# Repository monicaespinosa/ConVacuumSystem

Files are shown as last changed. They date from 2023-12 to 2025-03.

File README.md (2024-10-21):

# ConVacuumSystem
Later I will have time to explain what this is about. Let's start with the important things.

## Current circuit
The circuit (still to try) goes as following:



The setup still has to be simulated to find out V_c and to check the accuracy of the voltages selected for the grid and the plate.

## CST Simulations of the setup
The following setup was simulated:


Initially were the following voltages set:
* V_S 6.4 V
* V_C: 6.4 V
* V_G= 400 V
* V_P= 1000 V

The result for the obtained trajectory is shown below. The obtained current was around 5 mA.



However, the shape of the electron beams seems to change its shape in a very drastic way. Making the V_C smaller (more negative) should help concentring more the electrons to the center of the beam. A second simulation was made sweeping the voltage of the Wehnelt_Cylinider between -10 V and 6 V. 

As a result, the following charges on the plate were obtained:


Particles that come out of the coil:


They are only high when the voltage at the Wehnelt Cylinider is equal or higher than that of the coil. A new simulation sweeping Vc between 6.4V and 15.4V is been made. Results:



Evidently, the current (and as a consequence the particles getting to the plate) exists only when V_C>=V_S. The trajectories of the particles change however as they seem to be pushed into the cylinder (because of the higher voltage):



A new simulation setting the voltage on the grid V_G=800 V, putting a porcelain cylinder around the components (to simulate the glass cylinider) and moving the cylinider along the z-axis was made. The obtained trajectories are:



### Setting the voltage on the plate nearly to 0
Simulation with V_G = 1000 V and V_P = 4 V, and moving the cylinder to its initial position.



Simulation with the same parameters but moving the cylinder so its positioned closer to the plate.



Final simulation moving the cylinder back again and setting its voltage to -V_S.



### Variations of the voltage on the plate

Current incoming to the plate is the import_2 current.


Incoming particles:


### Changing the cathode
For all the following simulations the following voltages are set: V_S=6.4V, V_C=-30V V_G = 1000V and V_P = 4V.

#### Vertical filled PEC cylinder
Model:



Trajectories:



Total current leaving the cathode: 1.191e-03 mA

### Vertical hollow PEC cylinder
The cathode looks like the one before but is hollow with a thickness of 0.3 mm.

Trajectories:



Total current leaving the cathode: 9.14e-02 mA

### Toroid
Model:



Trajectories:



Total current leaving the cathode: 0.98 mA

### Rectangular cathode:
Model:



Trajectories: 



Total current leaving the cathode: 0.78 mA

### Sphere
Model:



Trajectories:



Total current leaving the cathode: 1.19 mA

### cut Cone:
Model:



It didn't emit any current when being put this way. However, when rotating like this:



The following trajectories are gotten:



Total current leaving the cathode: 0.71 mA

### Electron-gun Cathode
Model: 



It's a "cone" whose two planar circular faces are connected not by a rotated linear surface but a rotated exponential surface so it's internal radious get's thicker in an exponential way along the w axis as w decreases, simulating a pointy trunked cone. It was initially made small but only few particles were accelerated. Increasing its size and getting it closer to the grid produces the following trajectories:



The total current leaving the cathode was 9.35 mA. However the trajectories are messy and very disperse. After trying to move both the cathode and the grid further from the plate, because of the Wehnelt-Cylinder, the particles collide and then get dispersed again, without reaching the plate:



### Toroid-Coil

Model:

Trajectories: (actually a pretty straight beam)



However, the current incoming to the plate was not as high as expected. In this case, a variation of the voltage on the plate was made and the following curve obtained:



A dependency of the current to the voltage on the grid was also tested. The results below show in fact that the highest this voltage is, the highest the current.



As the shape of the beam seems to be well centered, another try using two toroids was given a shot. The model of the cathode goes as following:



As expected, the trajectories:



However the current across the platte is 50 uA. 

### Clapton Coil
This is the coil used normally for vapers. One of these was modelled in CST and looks like this:




The current incoming into the plate is 21.46uA. However, as the clapton coils that are found in the market have typically a diameter of 3.0mm, which for this project is too small. In order to increase the size of the cathode, a few of them can be placed together. For this purpose, four clapton coils forming a loop was simulated:



Trajectories: Not so straight directed to the center of the beam.



Current incoming to the plate: 0.18 mA

## Current measurement

### Methode
As mentioned before, this is the electrical structure of the setup:



The current measurement in between the plate and the voltage source V_p is more detailed here:



The current flowing through R_mess is theorically expected to be around 5mA according to the simulations. Supposing that the current is 10mA, the following circuit was simulated to choose the value of R_mess:





The voltage across Rm increases as Rm does. A value of Rm=140 ohm is temporarily chosen.

The following component is a amplifier that measures the voltage across the resistor R_mess and whose output is a digital signal whose amount of 1's is proportional to the current flowing through R_mess. The used amplifier is the Si8946A, that measures voltages between -62.5 mV and +62.5 mV, and whose output has a frequency of 10MHz. As this frequency is too high for a microcontroller like Arduino to read, a phase of signal conditioning is required. The simple RC filter produces an analog signal which corresponds to an average value of the quantity of 1's contained in the digital output of the amplifier. As this output is either a 0 or a 1, the analog response of the filter varies between 0V to 1V. However, as we intend to read this signal with Arduino, in order to take of advantage of all its measuring range the to-be-measured signal should be in the full range of 0V to 5V. This is the reason why an additional operational amplifier with a gain of 5 is used. The amplifier corresponds to the TLV9001 by Texas Instruments.

### PCB

The whole circuitry mentioned above, intended to be used for measuring the current caused by the electrons colliding into the plate and further flowing through R_mess, will be designed to be as close as posible to the plate. As not only the amount of current is important, but also the distribution of the electrons along the plate, this last is eventually going to be divided into many smaller plates whose incoming current will be measured separatedly. The first PCB designed to try the measuring circuitry has three plates. The PCB has two layers, one of them containing the plates



and the other one the Si8946A amplifiers and the connector in charge of providing feeding voltage and of letting the signals out. 



To know if the digital signal at 10 MHz is able to be carried by a normal jumper cable without using a SMA connector, some calculations need to be made:

Let's assume a square wave and use Bogatins rule of thumb [here](https://www.edn.com/rule-of-thumb-1-bandwidth-of-a-signal-from-its-rise-time/). According to the datasheet, the rise time is 20ns. The bandwidth of such a signal is 50 MHz, whose wavelength in free space is 6m, let's say 3m in the PCB. At 1/10th wavelength that's 30cm, which sets the upper limit to the jumper wire's length. 

Another option is to attach a second PCB using a PCB to PCB connector. 

>>>>>>> main

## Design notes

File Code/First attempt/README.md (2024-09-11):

At this moment, the Arduino Code has 4 functions: 
1) Communicate with the TC110 usisng the RS485 protocol and register all relevant data about the turbopump. 
2) Read the external pressure sensor. 
3) Display the relevant data of the system in a external LCD
4) receive an user input to modify the settings of the pump

functions 3 and 4 are needed for the system to be fully independant from a computer.

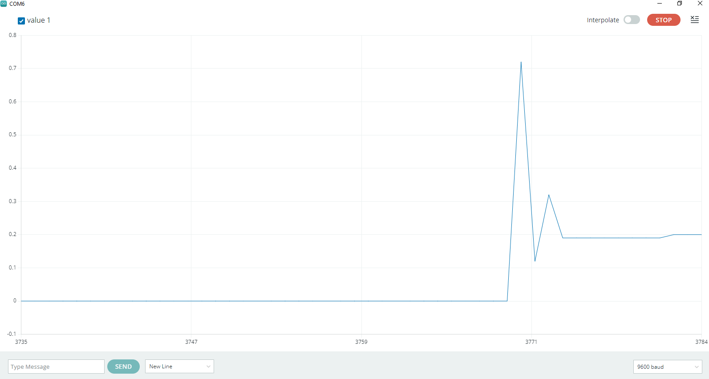
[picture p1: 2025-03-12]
Capture.PNG

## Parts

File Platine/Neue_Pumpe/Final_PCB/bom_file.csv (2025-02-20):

Reference | Value | Datasheet | Footprint | Qty | DNP
C1,C2,C3,C4,C5,C6,C7,C8,C9,C10,C11,C12,C13,C14,C15,C16,C17,C18 | 100p | ~ | Capacitor_SMD:C_0603_1608Metric_Pad1.08x0.95mm_HandSolder | 18
C20,C21 | 100n | ~ | Capacitor_SMD:C_0603_1608Metric_Pad1.08x0.95mm_HandSolder | 2
C22,C23 | 10u | ~ | Capacitor_SMD:C_0603_1608Metric_Pad1.08x0.95mm_HandSolder | 2
C24,C25,C27,C28,C29,C30,C31,C32,C34,C35,C36,C37,C38,C39,C40,C41 | 0.1uF | ~ | Capacitor_SMD:C_0603_1608Metric_Pad1.08x0.95mm_HandSolder | 16
C42,C43,C44,C45,C46,C47,C48,C49,C50 | 10n | ~ | Capacitor_SMD:C_0603_1608Metric_Pad1.08x0.95mm_HandSolder | 9
J1 | Conn_01x12 | ~ | SHF-106-01-L-D-SM:SHF-106-01-L-D-SM | 1
J2,J3,J4,J5 | Conn_01x10 | ~ | -- verschiedene Werte -- | 4
J6,J8 | Conn_01x08 | ~ | -- verschiedene Werte -- | 2
J7,J9 | Conn_01x06 | ~ | -- verschiedene Werte -- | 2
J10 | Conn_01x02 | ~ | OSTTE020104:OST_OSTTE020104 | 1
R1,R2,R7,R8,R9,R10,R19,R20,R21,R22,R23,R24,R37,R38,R39,R40,R41,R42,R64,R65,R66,R67,R68,R69,R70,R71,R72 | 1k | ~ | Resistor_SMD:R_0603_1608Metric_Pad0.98x0.95mm_HandSolder | 27
R3,R4,R11,R12,R13,R14,R25,R26,R27,R28,R29,R30,R43,R44,R45,R46,R47,R48 | 100k | ~ | Resistor_SMD:R_0603_1608Metric_Pad0.98x0.95mm_HandSolder | 18
R5,R6,R15,R16,R17,R18,R31,R32,R33,R34,R35,R36,R49,R50,R51,R52,R53,R54 | 252k | ~ | Resistor_SMD:R_0603_1608Metric_Pad0.98x0.95mm_HandSolder | 18
R55,R56,R57,R58,R59,R60,R61,R62,R63 | 12.5 | ~ | Resistor_SMD:R_0603_1608Metric_Pad0.98x0.95mm_HandSolder | 9
U1,U2,U3,U4,U5,U6,U7,U8,U9,U10,U11,U12,U13 | ~ |  | -- verschiedene Werte -- | 13

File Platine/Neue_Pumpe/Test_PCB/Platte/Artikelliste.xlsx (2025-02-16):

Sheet: Tabelle1
Artikelnummer | Bezeichnung | Menge | Einheit | Einzelpreis (netto) | Lieferantennummer | B/N
200-FLE10501GDVKTR | Platine-zu-Platine & Mezzanine-Steckverbinder Cost Effective Surface Mount Socket, 0.050" Pitch | 4 | Stck | 2.30 |  |  | Mouser
200-FTSH10501LDVK | Sockel & Kabelgehäuse High Reliability Header Strips, .050" pitch | 4 | Stck | 2.36 |  |  | Mouser
667-ERA-3AEB2800V | Dünnfilmwiderstände - SMD 0603 280ohm 0.1% 25ppm | 20 | Stck | 0.07 |  |  | Mouser

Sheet: Tabelle2
Stck
VPE
Kanister
Kartons
KG
Liter
m
m²
Paar
Pckg
Sq Inch
AE
Std
USG
Fass

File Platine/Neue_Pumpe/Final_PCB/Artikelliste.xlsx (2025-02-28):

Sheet: Tabelle1
Artikelnummer | Bezeichnung | Menge | Einheit | Einzelpreis (netto) | Lieferantennummer | B/N
200-SHF10601LDSM | Headers & Wire Housings Shrouded Terminal Strip, 0.050" pitch | 2 | Stck | 2.83 |  |  | Mouser | final connector
200-FFSD06D06.0001N | Ribbon Cables / IDC Cables .050" Low Profile Tiger Eye IDC Ribbon Cable Assembly | 2 | Stck | 11.17 |  |  | Mouser | final connector cable
200-FLE10501GDVKTR | Board to Board & Mezzanine Connectors Cost Effective Surface Mount Socket, 0.050" Pitch | 4 | Stck | 2.3 |  |  | Mouser | anode connector
200-FTSH10501LDVK | Headers & Wire Housings High Reliability Header Strips, .050" pitch | 2 | Stck | 2.36 |  |  | Mouser | from anode to sensor PCB conector
ED2740-ND | TERM BLK 2POS SIDE ENT 3.5MM PCB | 2 | Stck | 0.46 |  |  | Digikey | bornera
634-SI8946ABIS | SI8946AB-IS | 6 | Stck | 3.94 |  |  | Mouser | sensors
80-C0603C101J5TAUTO | Kondensator aus mehreren Keramikschichten MLCC - SMD/SMT 100.PF | 10 | Stck | 0.034 |  |  | Mouser | cond 100p
603-RT0603BRD071KL | Dünnfilmwiderstände - SMD 1KOhms 0603 5ppm 0.1% Precision | 20 | Stck | 1.31 |  |  | Mouser | res 1k
603-RT0603BRD07100KL | Dünnfilmwiderstände - SMD PLT0603 5PPM 100K 0.1% | 10 | Stck | 4.95 |  |  | Mouser | res 100k
667-ERA-3AEB2553V | Dünnfilmwiderstände - SMD 1/10W 255K Ohms 0.1% | 10 | Stck | 0.097 |  |  | Mouser | res 255k
279-CPF0201B280RE1 | Thin Film Resistors - SMD CPF 0201 280R 0.1% 25ppm 1K RL | 20 | Stck | 0.565 |  |  | Mouser | res 280
80-C0603X103F3GACTU | Kondensator MLCC - SMD/SMT 25V 0.01uF C0G 0603 1% | 10 | Stck | 0.759 |  |  | Mouser | cond 10n
200-FLE10701GDVKTR | Board to Board & Mezzanine Connectors Cost Effective Surface Mount Socket, 0.050" Pitch | 2 | Stck | 2.59 |  |  | Mouser | for past PCB - female conector
200-FTSH10701LDVK | Board to Board & Mezzanine Connectors Cost Effective Surface Mount Socket, 0.050" Pitch | 4 | Stck | 2.59 |  |  | Mouser | for new and past PCB - smd male conector
200-FFMD07T020001N | Ribbon Cables / IDC Cables .050" Tiger Eye IDC Ribbon Cable Assemblies, Terminal/Socket | 2 | Stck | 9.18 |  |  | Mouser | for past PCB - cable (male/female)
200-FTS10701LDP | Headers & Wire Housings Micro Low Profile Header Strips | 2 | Stck | 2.29 |  |  | Mouser | for new PCB - TH female conector
200-FFSD07D02.0001N | Ribbon Cables / IDC Cables .050" Low Profile Tiger Eye IDC Ribbon Cable Assembly | 2 | Stck | 10.85 |  |  | Mouser | for new PCB - cable (female-female)
 |  |  |  |  |  |  |  | No amps op, no dc dc converter needed
200-FFMD07T059001N | Flachkabel/IDC-Kabel .050" Tiger Eye IDC Ribbon Cable Assemblies, Terminal/Socket | 2 | Stck | 9,3 |  |  | Mouser | instead of the one in row 16
71-TNPW0603252RBEEN | Dünnfilmwiderstände - SMD 252ohms .1% 25ppm | 10 | Stck | 0,884 |  |  | Mouser | instead of the one in row 11

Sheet: Tabelle2
Stck
VPE
Kanister
Kartons
KG
Liter
m
m²
Paar
Pckg
Sq Inch
AE
Std
USG
Fass

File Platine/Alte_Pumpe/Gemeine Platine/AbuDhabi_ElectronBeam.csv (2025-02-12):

Source: | \\flexo\dasadirs\Kaesbach\Temp\AbuDhabi_ElectronBeam\AbuDhabi_ElectronBeam.kicad_sch
Date: | 21.02.2024 17:27:44
Tool: | Eeschema 7.0.1
Generator: | C:\Program Files\KiCad\7.0\bin\scripting\plugins/bom_csv_grouped_by_value.py
Component Count: | 53
Collated Components:
Item | Qty | Reference(s) | Value | LibPart | Footprint | Datasheet | DNP | Availability | Check_prices | Description | MF | MP | Package | Price | Sim.Device | Sim.Pins | SnapEDA_Link
1 | 1 | A3 | Arduino_Mega2560_R3_Shield | arduino-library:Arduino_Mega2560_R3_Shield | Arduino:Arduino_Mega2560_R3_Shield | https://docs.arduino.cc/hardware/mega-2560
2 | 7 | C1, C3, C4, C5, C7, C8, C9 | 0.1u | Device:C | Capacitor_SMD:C_0603_1608Metric | ~
3 | 2 | C2, C6 | .1u | Device:C | Capacitor_SMD:C_0603_1608Metric | ~
4 | 5 | D1, D2, D3, D4, D6 | LED | Device:LED | LED_SMD:LED_0603_1608Metric_Pad1.05x0.95mm_HandSolder | ~
5 | 4 | D5, D9, D10, D11 | LED | Device:LED | LED_SMD:LED_0603_1608Metric | ~
6 | 1 | D7 | D | Device:D | LED_SMD:LED_0603_1608Metric_Pad1.05x0.95mm_HandSolder | ~ |  |  |  |  |  |  |  |  | D | 1=K 2=A
7 | 1 | J1 | Comms | Connector:Conn_01x04_Socket | Connector_PinSocket_2.54mm:PinSocket_1x04_P2.54mm_Vertical | ~
8 | 1 | J2 | Opt. ext. Ausgangsspannung | Connector:Conn_01x03_Socket | Connector_PinSocket_2.54mm:PinSocket_1x03_P2.54mm_Vertical | ~
9 | 1 | J3 | Opt. Ard. Ausgangspannung | Connector:Conn_01x03_Socket | Connector_PinSocket_2.54mm:PinSocket_1x03_P2.54mm_Vertical | ~
10 | 1 | J12 | Sensor | :Conn_01x04_Female_1 | Connector_JST:JST_EH_B4B-EH-A_1x04_P2.50mm_Vertical | ~
11 | 1 | J13 | Bomba | :Conn_01x04_Female_1 | Connector_JST:JST_EH_B4B-EH-A_1x04_P2.50mm_Vertical | ~
12 | 1 | J16 | Power | Connector:Conn_01x02_Female | Connector_PinSocket_2.54mm:PinSocket_1x02_P2.54mm_Vertical | ~
13 | 1 | J18 | Buttons | Connector:Conn_01x04_Female | Connector_PinSocket_2.54mm:PinSocket_1x04_P2.54mm_Vertical | ~
14 | 1 | J19 | Ext. versorgung conn | Connector_Generic:Conn_01x02 | Connector_JST:JST_EH_B2B-EH-A_1x02_P2.50mm_Vertical | ~
15 | 3 | R1, R3, R4 | 1k | Device:R | Resistor_SMD:R_0603_1608Metric_Pad0.98x0.95mm_HandSolder | ~
16 | 6 | R2, R5, R6, R9, R10, R11 | 1k | Device:R | Resistor_SMD:R_0603_1608Metric | ~
17 | 4 | R7, R8, R13, R14 | 4.7k | Device:R | Resistor_SMD:R_0603_1608Metric | ~
18 | 4 | R12, R18, R19, R20 | 10k | Device:R | Resistor_SMD:R_0603_1608Metric | ~
19 | 2 | R15, R16 | 10 | Device:R | Resistor_SMD:R_0603_1608Metric | ~
20 | 1 | R17 | 120 | Device:R | Resistor_SMD:R_0603_1608Metric | ~
21 | 1 | U1 | 74LS01 | MM74HC:MM74HC00M | Package_SO:SOIC-14_3.9x8.7mm_P1.27mm | http://www.nteinc.com/specs/7400to7499/pdf/nte74LS01.pdf
22 | 1 | U2 | L7805 | Regulator_Linear:L7805 | Package_TO_SOT_THT:TO-220-3_Vertical | http://www.st.com/content/ccc/resource/technical/document/datasheet/41/4f/b3/b0/12/d4/47/88/CD00000444.pdf/files/CD00000444.pdf/jcr:content/translations/en.CD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
23 | 1 | U3 | MAX3232 | Interface_UART:MAX3232 | Package_SO:SOIC-16_3.9x9.9mm_P1.27mm | https://datasheets.maximintegrated.com/en/ds/MAX3222-MAX3241.pdf
24 | 1 | U4 | MAX485ESA_T | MAX485ESA_T:MAX485ESA_T | MAX485:SOIC127P600X175-8N |  |  | In Stock | https://www.snapeda.com/parts/MAX485ESA+T/Analog+Devices/view-part/?ref=eda | Low-Power, Slew-Rate-Limited RS-485/RS-422 Transceivers | Analog Devices | MAX485ESA+T | SOIC-8 Maxim | None |  |  | https://www.snapeda.com/parts/MAX485ESA+T/Analog+Devices/view-part/?ref=snap
25 | 1 | U6 | 74LS20 | 74ls20D:74LS20 | Package_SO:SOIC-14_3.9x8.7mm_P1.27mm | http://www.ti.com/lit/gpn/sn74LS20

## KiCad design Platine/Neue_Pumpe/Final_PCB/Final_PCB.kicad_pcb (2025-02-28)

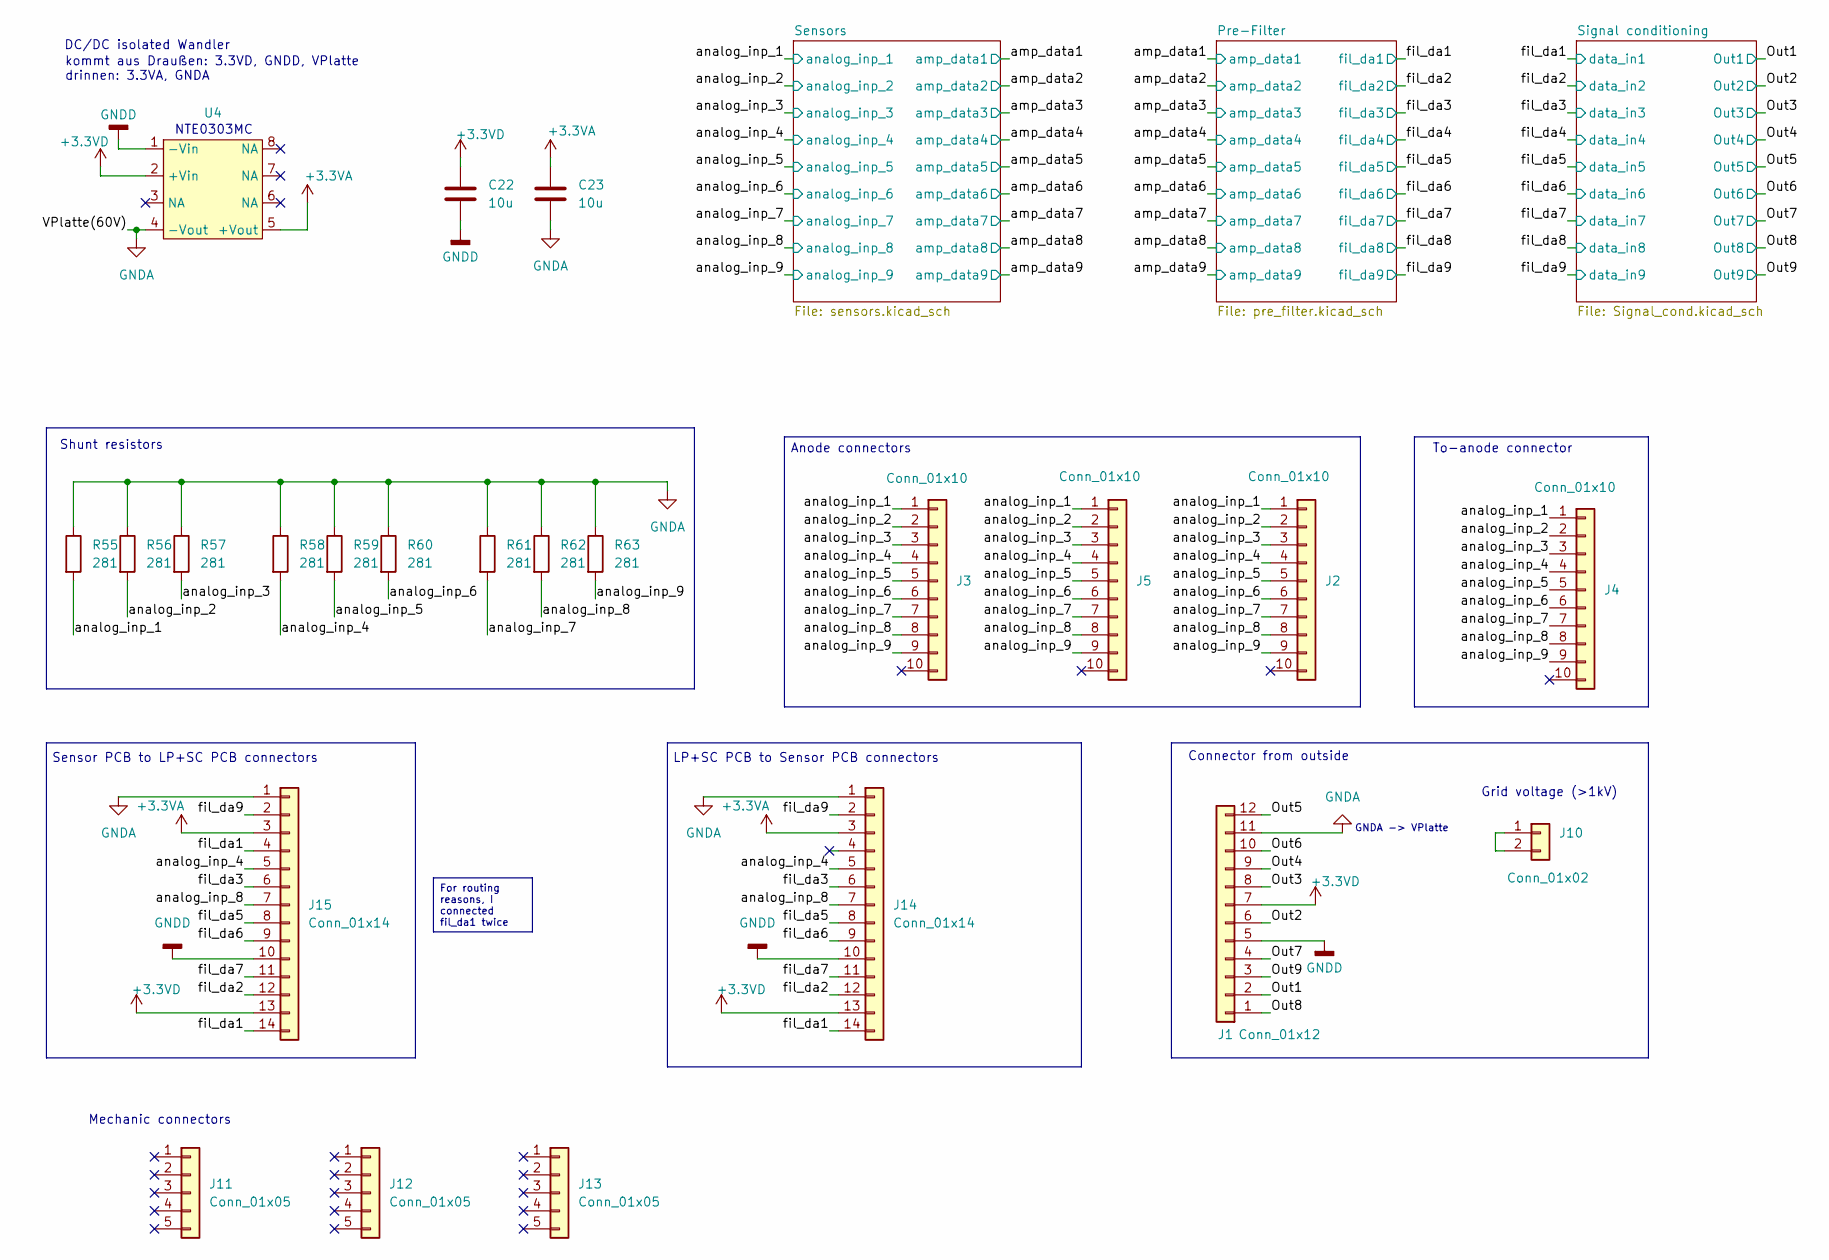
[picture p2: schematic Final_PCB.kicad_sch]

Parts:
C22, C23: 10u; C_0603_1608Metric_Pad1.08x0.95mm_HandSolder
J1: Conn_01x12; SHF-106-01-L-D-SM
J2, J3, J5: Conn_01x10; FLE-105-01-X-DV-Y-TR
J4: Conn_01x10; FTSH-105-01-L-DV-K
J10: Conn_01x02; OST_OSTTE020104
J11, J12, J13: Conn_01x05; PinHeader_1x05_P1.27mm_Vertical
J14: Conn_01x14; SAMTEC_FTS-107-01-L-D
J15: Conn_01x14; SAMTEC_FTSH-107-01-L-DV-K
R55, R56, R57, R58, R59, R60, R61, R62, R63: 281; R_0603_1608Metric_Pad0.98x0.95mm_HandSolder
U4: SMDIP-8_W9.53mm

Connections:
+3.3VA: C23.2, J14.3, J15.3, U4.5 (+Vout); also elsewhere on the board
+3.3VD: C22.2, J1.7, J14.13, J15.13, U4.2 (+Vin); also elsewhere on the board
/Out1: J1.2; also elsewhere on the board
/Out2: J1.6; also elsewhere on the board
/Out3: J1.8; also elsewhere on the board
/Out4: J1.9; also elsewhere on the board
/Out5: J1.12; also elsewhere on the board
/Out6: J1.10; also elsewhere on the board
/Out7: J1.4; also elsewhere on the board
/Out8: J1.1; also elsewhere on the board
/Out9: J1.3; also elsewhere on the board
/analog_inp_1: J2.1, J3.1, J4.1, J5.1, R55.2; also elsewhere on the board
/analog_inp_2: J2.2, J3.2, J4.2, J5.2, R56.2; also elsewhere on the board
/analog_inp_3: J2.3, J3.3, J4.3, J5.3, R57.2; also elsewhere on the board
/analog_inp_4: J2.4, J3.4, J4.4, J5.4, J14.5, J15.5, R58.2; also elsewhere on the board
/analog_inp_5: J2.5, J3.5, J4.5, J5.5, R59.2; also elsewhere on the board
/analog_inp_6: J2.6, J3.6, J4.6, J5.6, R60.2; also elsewhere on the board
/analog_inp_7: J2.7, J3.7, J4.7, J5.7, R61.2; also elsewhere on the board
/analog_inp_8: J2.8, J3.8, J4.8, J5.8, J14.7, J15.7, R62.2; also elsewhere on the board
/analog_inp_9: J2.9, J3.9, J4.9, J5.9, R63.2; also elsewhere on the board
/fil_da1: J14.14, J15.4, J15.14; also elsewhere on the board
/fil_da2: J14.12, J15.12; also elsewhere on the board
/fil_da3: J14.6, J15.6; also elsewhere on the board
/fil_da5: J14.8, J15.8; also elsewhere on the board
/fil_da6: J14.9, J15.9; also elsewhere on the board
/fil_da7: J14.11, J15.11; also elsewhere on the board
/fil_da9: J14.2, J15.2; also elsewhere on the board
GNDA: C23.1, J1.11, J14.1, J15.1, R55.1, R56.1, R57.1, R58.1, R59.1, R60.1, R61.1, R62.1, R63.1, U4.4 (-Vout); also elsewhere on the board
GNDD: C22.1, J1.5, J14.10, J15.10, U4.1 (-Vin); also elsewhere on the board
unnamed: J10.1, J10.2

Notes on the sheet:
For routing reasons, I connected fil_da1 twice
Anode connectors
GNDA -> VPlatte
Mechanic connectors
kommt aus Draußen: 3.3VD, GNDD, VPlatte drinnen: 3.3VA, GNDA
Shunt resistors
To-anode connector
Sensor PCB to LP+SC PCB connectors
LP+SC PCB to Sensor PCB connectors
Grid voltage (>1kV)
DC/DC isolated Wandler
Connector from outside
NTE0303MC

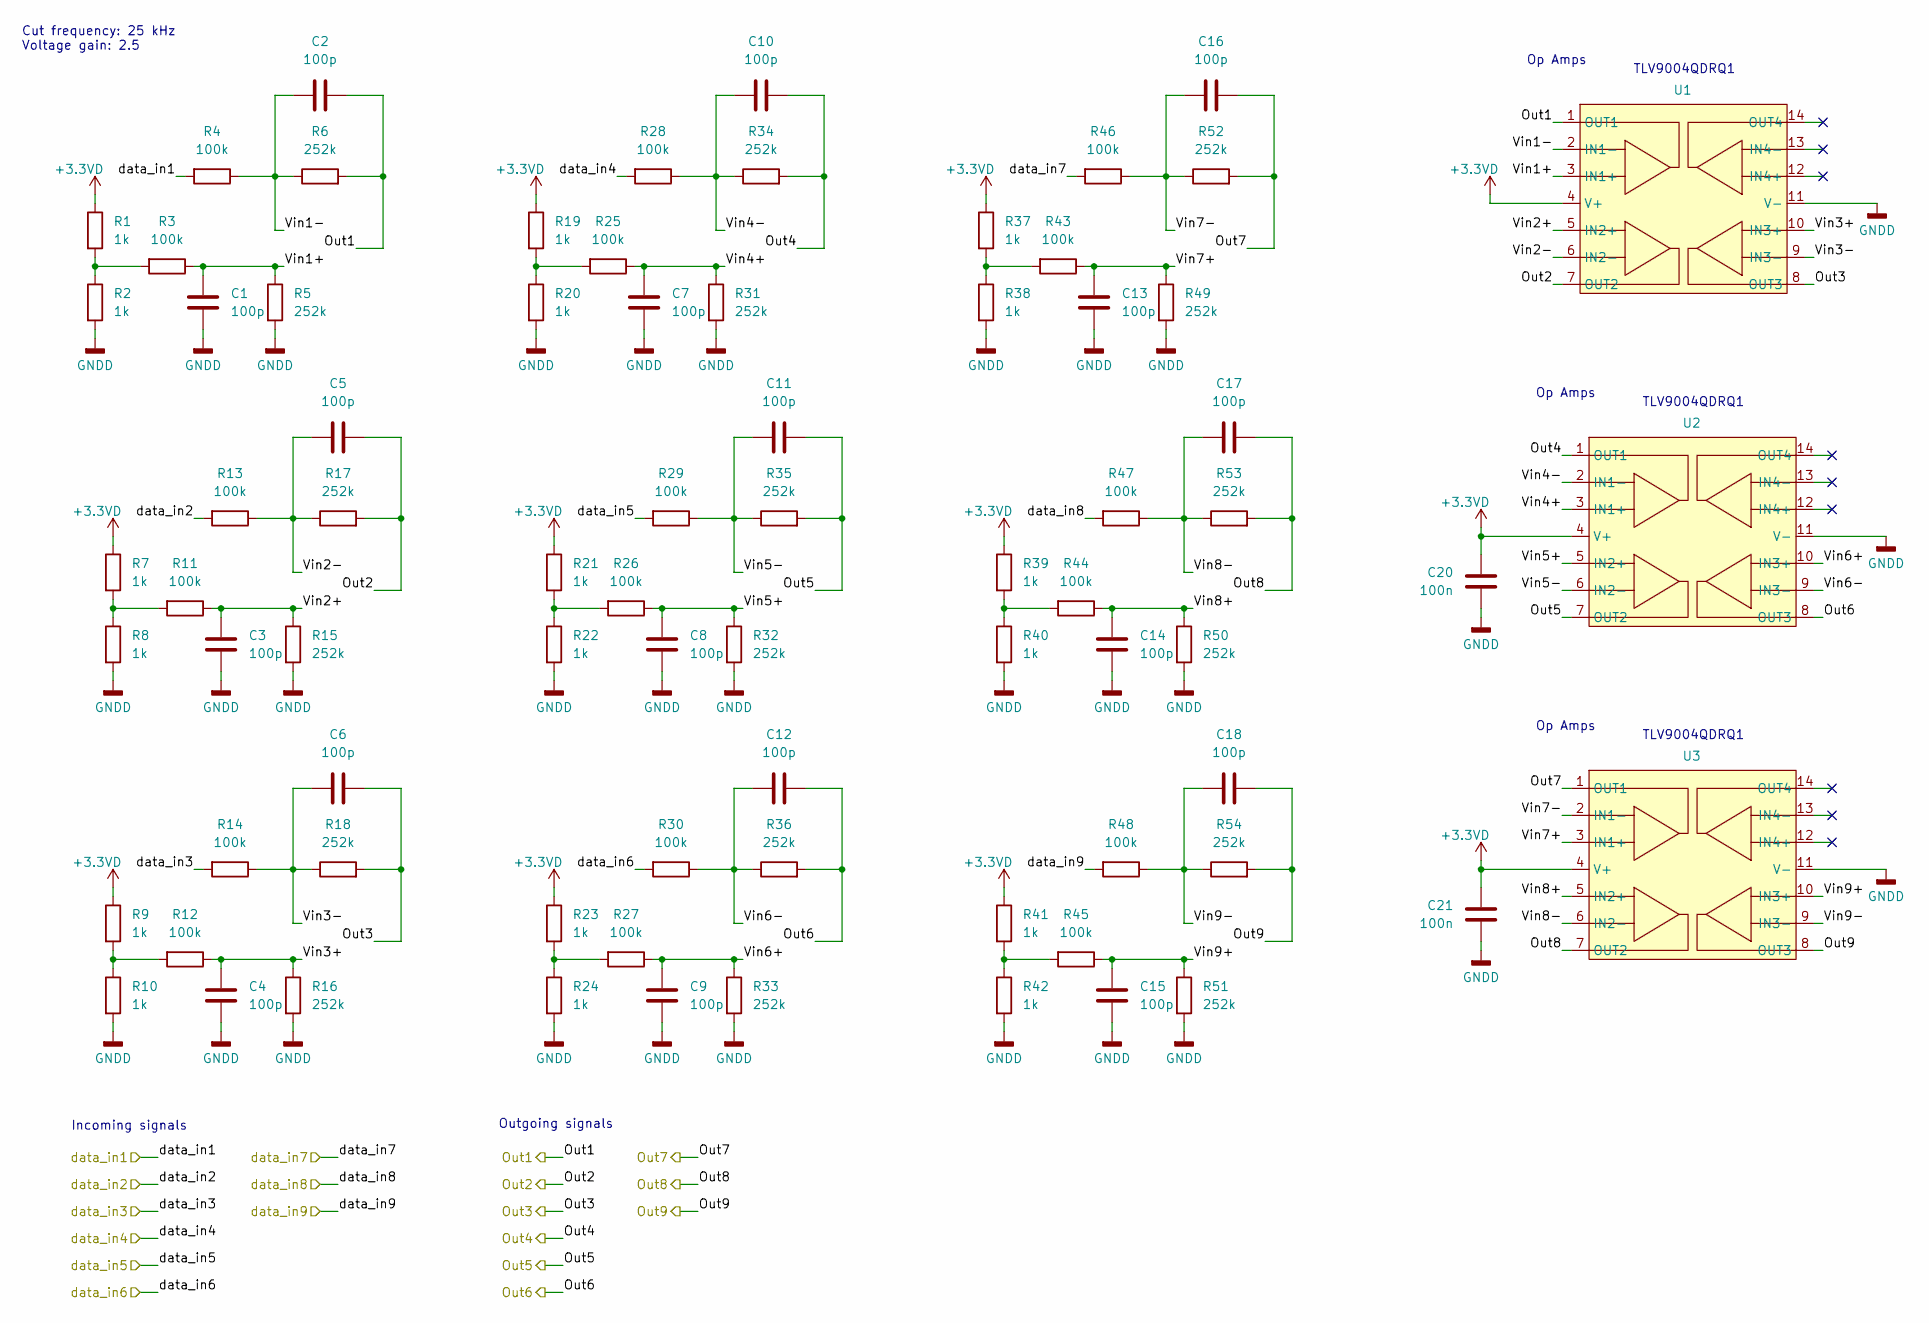
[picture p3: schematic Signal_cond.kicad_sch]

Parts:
C1, C2, C3, C4, C5, C6, C7, C8, C9, C10, C11, C12, C13, C14, C15, C16, C17, C18: 100p; C_0603_1608Metric_Pad1.08x0.95mm_HandSolder
C20, C21: 100n; C_0603_1608Metric_Pad1.08x0.95mm_HandSolder
R1, R2, R7, R8, R9, R10, R19, R20, R21, R22, R23, R24, R37, R38, R39, R40, R41, R42: 1k; R_0603_1608Metric_Pad0.98x0.95mm_HandSolder
R3, R4, R11, R12, R13, R14, R25, R26, R27, R28, R29, R30, R43, R44, R45, R46, R47, R48: 100k; R_0603_1608Metric_Pad0.98x0.95mm_HandSolder
R5, R6, R15, R16, R17, R18, R31, R32, R33, R34, R35, R36, R49, R50, R51, R52, R53, R54: 252k; R_0603_1608Metric_Pad0.98x0.95mm_HandSolder
U1, U2, U3: SOIC-14_3.9x8.7mm_P1.27mm

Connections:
+3.3VD: C20.2, C21.2, R1.1, R7.1, R9.1, R19.1, R21.1, R23.1, R37.1, R39.1, R41.1, U1.4 (V+), U2.4 (V+), U3.4 (V+); also elsewhere on the board
/Out1: C2.1, R6.2, U1.1 (OUT1); also elsewhere on the board
/Out2: C5.1, R17.2, U1.7 (OUT2); also elsewhere on the board
/Out3: C6.1, R18.2, U1.8 (OUT3); also elsewhere on the board
/Out4: C10.1, R34.2, U2.1 (OUT1); also elsewhere on the board
/Out5: C11.1, R35.2, U2.7 (OUT2); also elsewhere on the board
/Out6: C12.1, R36.2, U2.8 (OUT3); also elsewhere on the board
/Out7: C16.1, R52.2, U3.1 (OUT1); also elsewhere on the board
/Out8: C17.1, R53.2, U3.7 (OUT2); also elsewhere on the board
/Out9: C18.1, R54.2, U3.8 (OUT3); also elsewhere on the board
/Signal conditioning/Vin1+: C1.2, R3.1, R5.1, U1.3 (IN1+)
/Signal conditioning/Vin1-: C2.2, R4.1, R6.1, U1.2 (IN1-)
/Signal conditioning/Vin2+: C3.2, R11.1, R15.1, U1.5 (IN2+)
/Signal conditioning/Vin2-: C5.2, R13.1, R17.1, U1.6 (IN2-)
/Signal conditioning/Vin3+: C4.2, R12.1, R16.1, U1.10 (IN3+)
/Signal conditioning/Vin3-: C6.2, R14.1, R18.1, U1.9 (IN3-)
/Signal conditioning/Vin4+: C7.2, R25.1, R31.1, U2.3 (IN1+)
/Signal conditioning/Vin4-: C10.2, R28.1, R34.1, U2.2 (IN1-)
/Signal conditioning/Vin5+: C8.2, R26.1, R32.1, U2.5 (IN2+)
/Signal conditioning/Vin5-: C11.2, R29.1, R35.1, U2.6 (IN2-)
/Signal conditioning/Vin6+: C9.2, R27.1, R33.1, U2.10 (IN3+)
/Signal conditioning/Vin6-: C12.2, R30.1, R36.1, U2.9 (IN3-)
/Signal conditioning/Vin7+: C13.2, R43.1, R49.1, U3.3 (IN1+)
/Signal conditioning/Vin7-: C16.2, R46.1, R52.1, U3.2 (IN1-)
/Signal conditioning/Vin8+: C14.2, R44.1, R50.1, U3.5 (IN2+)
/Signal conditioning/Vin8-: C17.2, R47.1, R53.1, U3.6 (IN2-)
/Signal conditioning/Vin9+: C15.2, R45.1, R51.1, U3.10 (IN3+)
/Signal conditioning/Vin9-: C18.2, R48.1, R54.1, U3.9 (IN3-)
/fil_da1: R4.2; also elsewhere on the board
/fil_da2: R13.2; also elsewhere on the board
/fil_da3: R14.2; also elsewhere on the board
/fil_da4: R28.2; also elsewhere on the board
/fil_da5: R29.2; also elsewhere on the board
/fil_da6: R30.2; also elsewhere on the board
/fil_da7: R46.2; also elsewhere on the board
/fil_da8: R47.2; also elsewhere on the board
/fil_da9: R48.2; also elsewhere on the board
GNDD: C1.1, C3.1, C4.1, C7.1, C8.1, C9.1, C13.1, C14.1, C15.1, C20.1, C21.1, R2.2, R5.2, R8.2, R10.2, R15.2, R16.2, R20.2, R22.2, R24.2, R31.2, R32.2, R33.2, R38.2, R40.2, R42.2, R49.2, R50.2, R51.2, U1.11 (V-), U2.11 (V-), U3.11 (V-); also elsewhere on the board
unnamed: R1.2, R2.1, R3.2
unnamed: R9.2, R10.1, R12.2
unnamed: R7.2, R8.1, R11.2
unnamed: R19.2, R20.1, R25.2
unnamed: R21.2, R22.1, R26.2
unnamed: R23.2, R24.1, R27.2
unnamed: R37.2, R38.1, R43.2
unnamed: R39.2, R40.1, R44.2
unnamed: R41.2, R42.1, R45.2

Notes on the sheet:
Op Amps
Cut frequency: 25 kHz Voltage gain: 2.5
TLV9004QDRQ1
Outgoing signals
Incoming signals

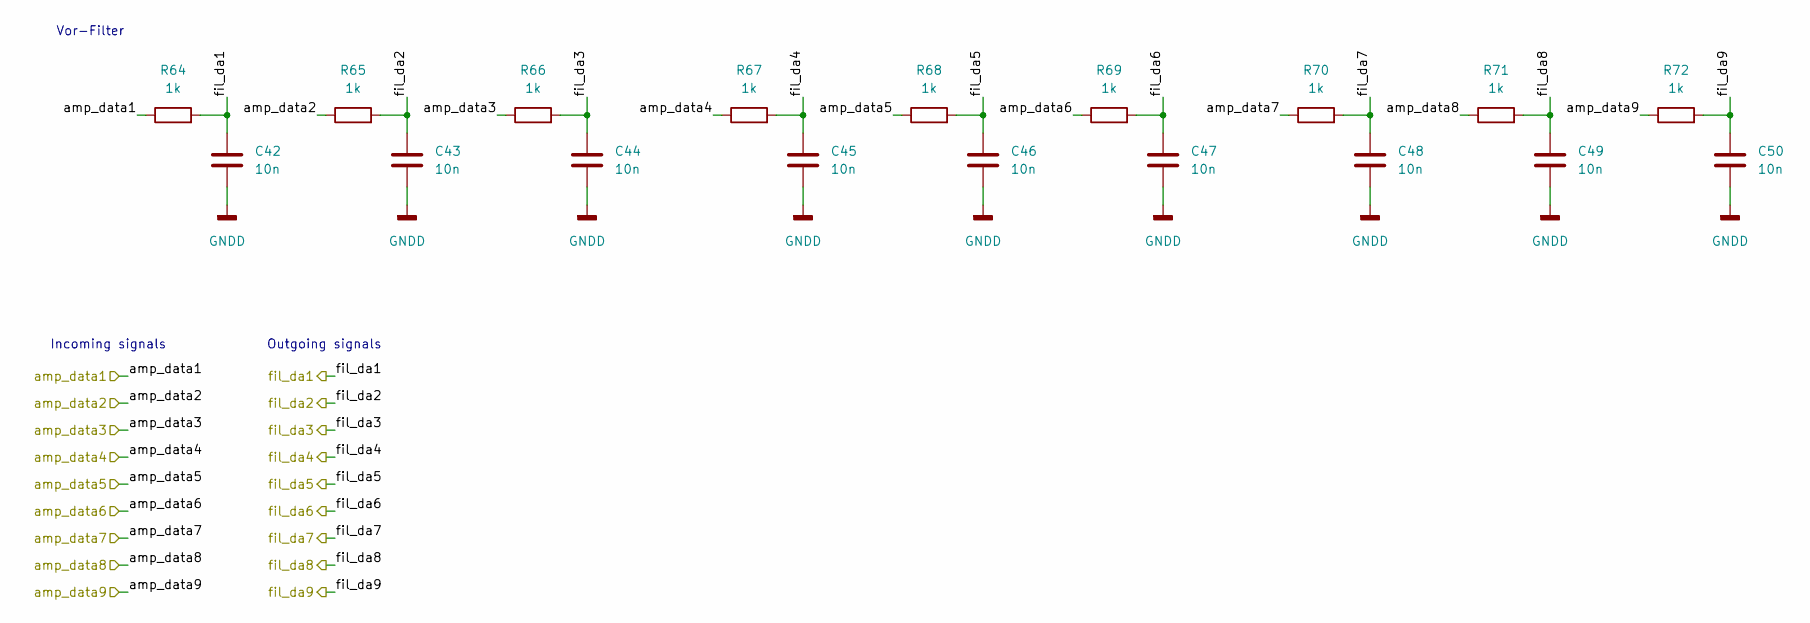
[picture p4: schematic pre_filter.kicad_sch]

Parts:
C42, C43, C44, C45, C46, C47, C48, C49, C50: 10n; C_0603_1608Metric_Pad1.08x0.95mm_HandSolder
R64, R65, R66, R67, R68, R69, R70, R71, R72: 1k; R_0603_1608Metric_Pad0.98x0.95mm_HandSolder

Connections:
/amp_data1: R64.1; also elsewhere on the board
/amp_data2: R65.1; also elsewhere on the board
/amp_data3: R66.1; also elsewhere on the board
/amp_data4: R67.1; also elsewhere on the board
/amp_data5: R68.1; also elsewhere on the board
/amp_data6: R69.1; also elsewhere on the board
/amp_data7: R70.1; also elsewhere on the board
/amp_data8: R71.1; also elsewhere on the board
/amp_data9: R72.1; also elsewhere on the board
/fil_da1: C42.1, R64.2; also elsewhere on the board
/fil_da2: C43.1, R65.2; also elsewhere on the board
/fil_da3: C44.1, R66.2; also elsewhere on the board
/fil_da4: C45.1, R67.2; also elsewhere on the board
/fil_da5: C46.1, R68.2; also elsewhere on the board
/fil_da6: C47.1, R69.2; also elsewhere on the board
/fil_da7: C48.1, R70.2; also elsewhere on the board
/fil_da8: C49.1, R71.2; also elsewhere on the board
/fil_da9: C50.1, R72.2; also elsewhere on the board
GNDD: C42.2, C43.2, C44.2, C45.2, C46.2, C47.2, C48.2, C49.2, C50.2; also elsewhere on the board

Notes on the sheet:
Vor-Filter
Outgoing signals
Incoming signals

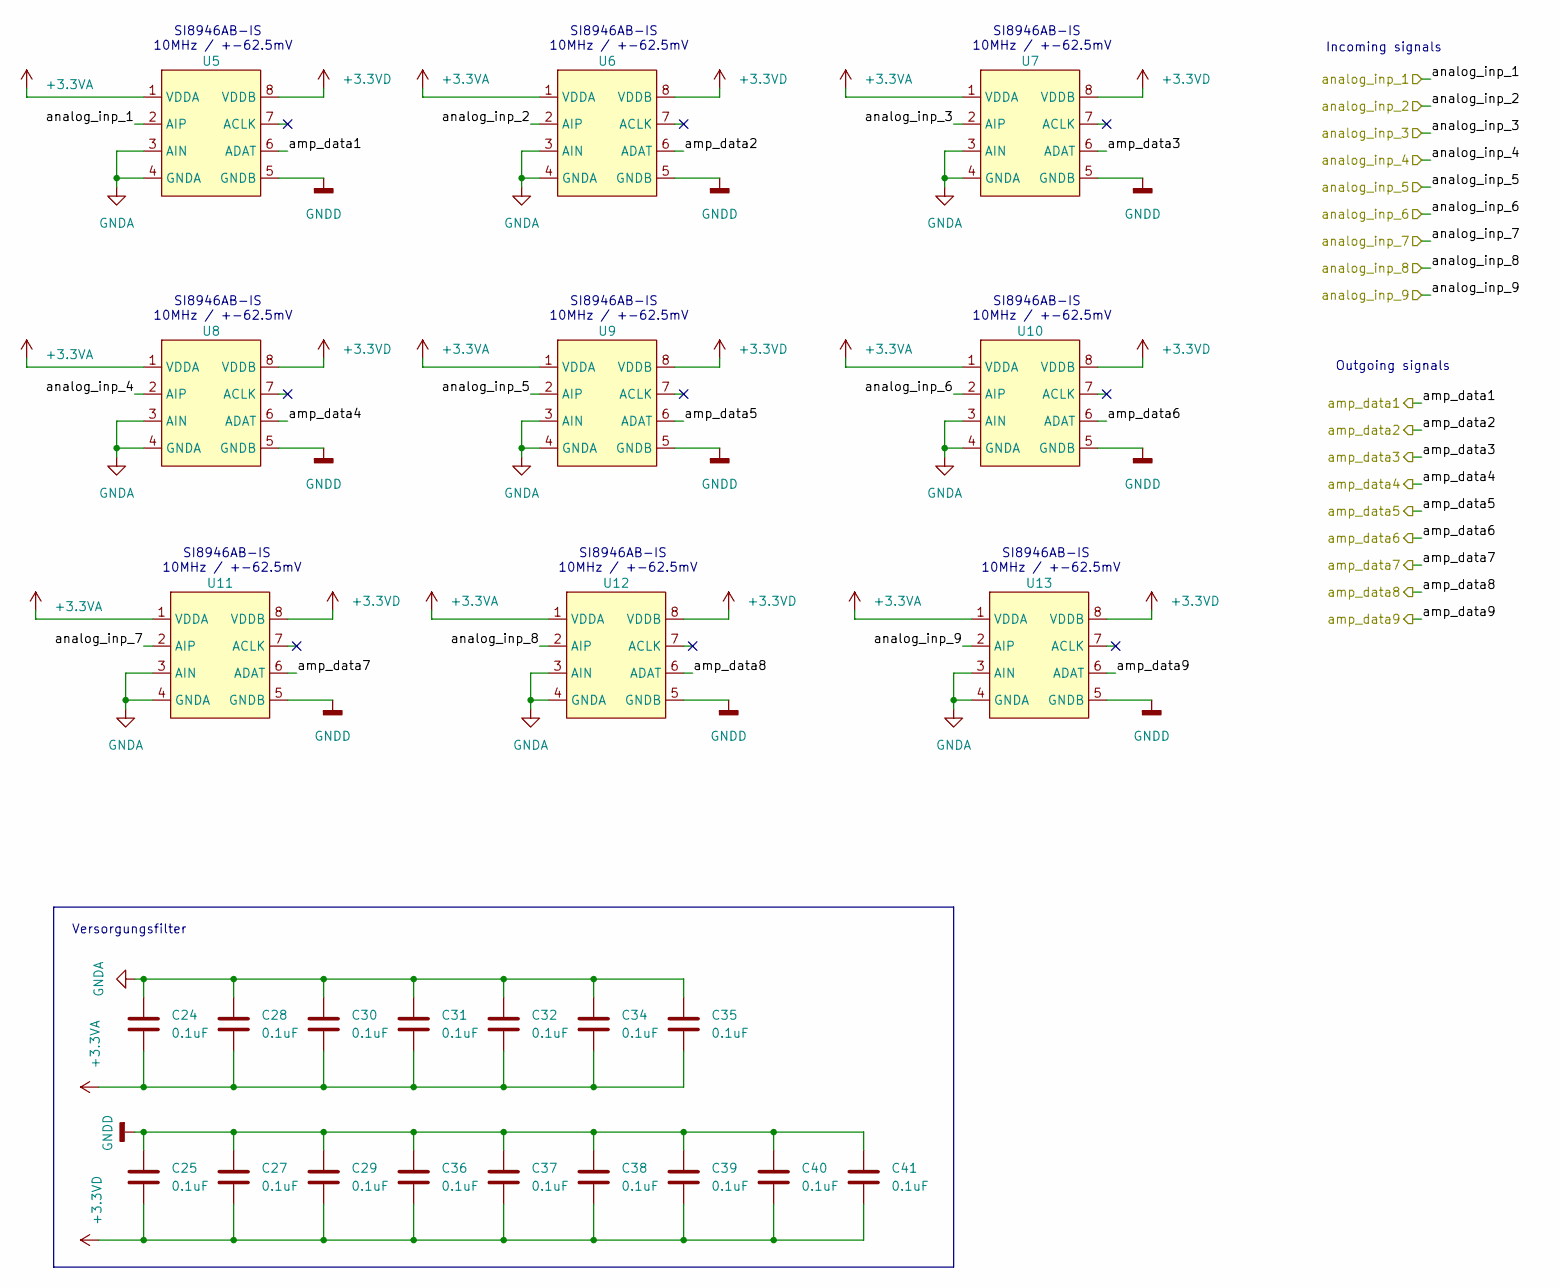
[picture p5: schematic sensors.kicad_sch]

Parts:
C24, C25, C27, C28, C29, C30, C31, C32, C34, C35, C36, C37, C38, C39, C40, C41: 0.1uF; C_0603_1608Metric_Pad1.08x0.95mm_HandSolder
U5, U6, U7, U8, U9, U10, U11, U12, U13: SOP-8_3.9x4.9mm_P1.27mm

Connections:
+3.3VA: C24.2, C28.2, C30.2, C31.2, C32.2, C34.2, C35.2, U5.1 (VDDA), U6.1 (VDDA), U7.1 (VDDA), U8.1 (VDDA), U9.1 (VDDA), U10.1 (VDDA), U11.1 (VDDA), U12.1 (VDDA), U13.1 (VDDA); also elsewhere on the board
+3.3VD: C25.2, C27.2, C29.2, C36.2, C37.2, C38.2, C39.2, C40.2, C41.2, U5.8 (VDDB), U6.8 (VDDB), U7.8 (VDDB), U8.8 (VDDB), U9.8 (VDDB), U10.8 (VDDB), U11.8 (VDDB), U12.8 (VDDB), U13.8 (VDDB); also elsewhere on the board
/amp_data1: U5.6 (ADAT); also elsewhere on the board
/amp_data2: U6.6 (ADAT); also elsewhere on the board
/amp_data3: U7.6 (ADAT); also elsewhere on the board
/amp_data4: U8.6 (ADAT); also elsewhere on the board
/amp_data5: U9.6 (ADAT); also elsewhere on the board
/amp_data6: U10.6 (ADAT); also elsewhere on the board
/amp_data7: U11.6 (ADAT); also elsewhere on the board
/amp_data8: U12.6 (ADAT); also elsewhere on the board
/amp_data9: U13.6 (ADAT); also elsewhere on the board
/analog_inp_1: U5.2 (AIP); also elsewhere on the board
/analog_inp_2: U6.2 (AIP); also elsewhere on the board
/analog_inp_3: U7.2 (AIP); also elsewhere on the board
/analog_inp_4: U8.2 (AIP); also elsewhere on the board
/analog_inp_5: U9.2 (AIP); also elsewhere on the board
/analog_inp_6: U10.2 (AIP); also elsewhere on the board
/analog_inp_7: U11.2 (AIP); also elsewhere on the board
/analog_inp_8: U12.2 (AIP); also elsewhere on the board
/analog_inp_9: U13.2 (AIP); also elsewhere on the board
GNDA: C24.1, C28.1, C30.1, C31.1, C32.1, C34.1, C35.1, U5.3 (AIN), U5.4 (GNDA), U6.3 (AIN), U6.4 (GNDA), U7.3 (AIN), U7.4 (GNDA), U8.3 (AIN), U8.4 (GNDA), U9.3 (AIN), U9.4 (GNDA), U10.3 (AIN), U10.4 (GNDA), U11.3 (AIN), U11.4 (GNDA), U12.3 (AIN), U12.4 (GNDA), U13.3 (AIN), U13.4 (GNDA); also elsewhere on the board
GNDD: C25.1, C27.1, C29.1, C36.1, C37.1, C38.1, C39.1, C40.1, C41.1, U5.5 (GNDB), U6.5 (GNDB), U7.5 (GNDB), U8.5 (GNDB), U9.5 (GNDB), U10.5 (GNDB), U11.5 (GNDB), U12.5 (GNDB), U13.5 (GNDB); also elsewhere on the board

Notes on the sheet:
Incoming signals
SI8946AB-IS 10MHz / +-62.5mV
Versorgungsfilter
Outgoing signals

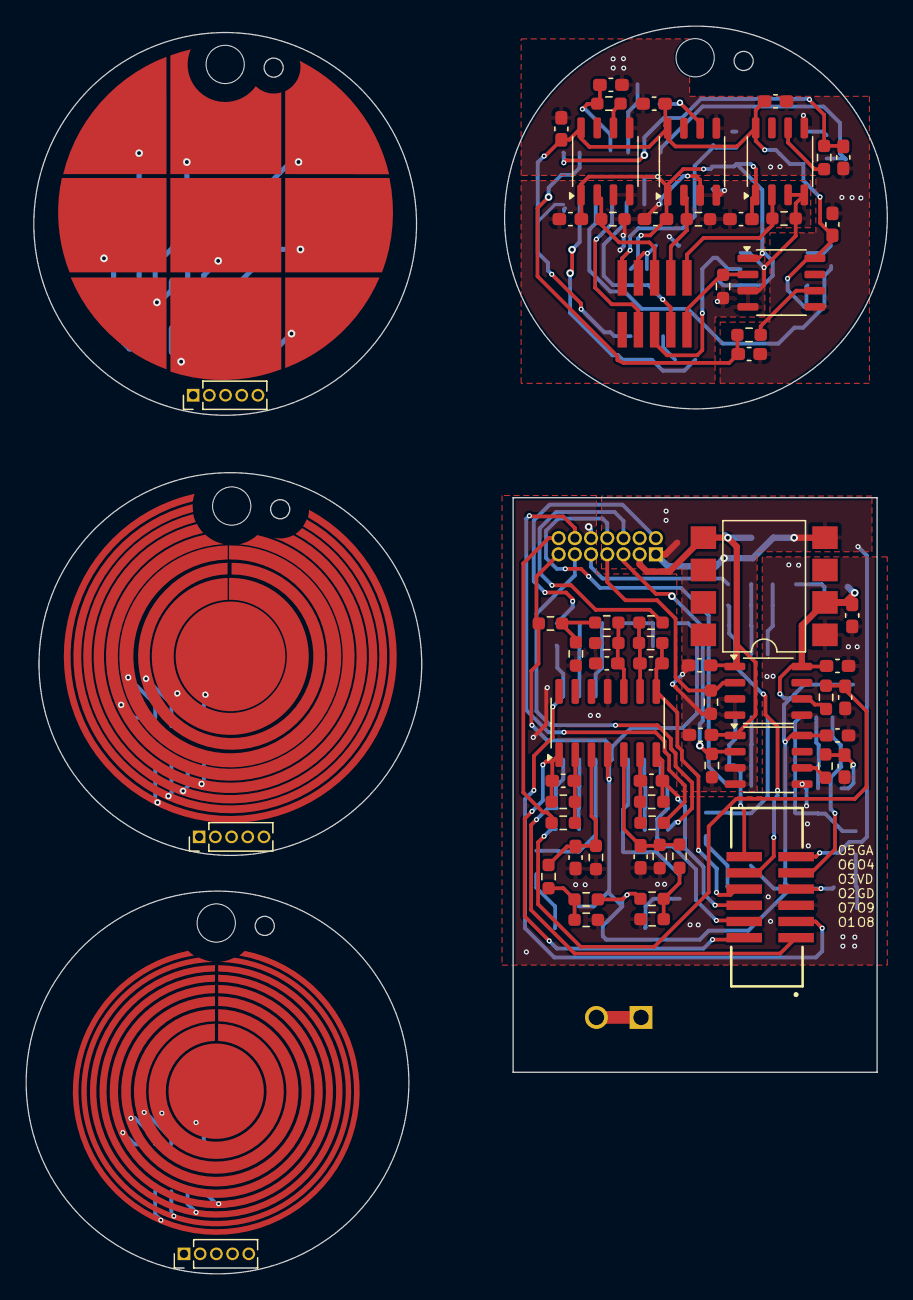
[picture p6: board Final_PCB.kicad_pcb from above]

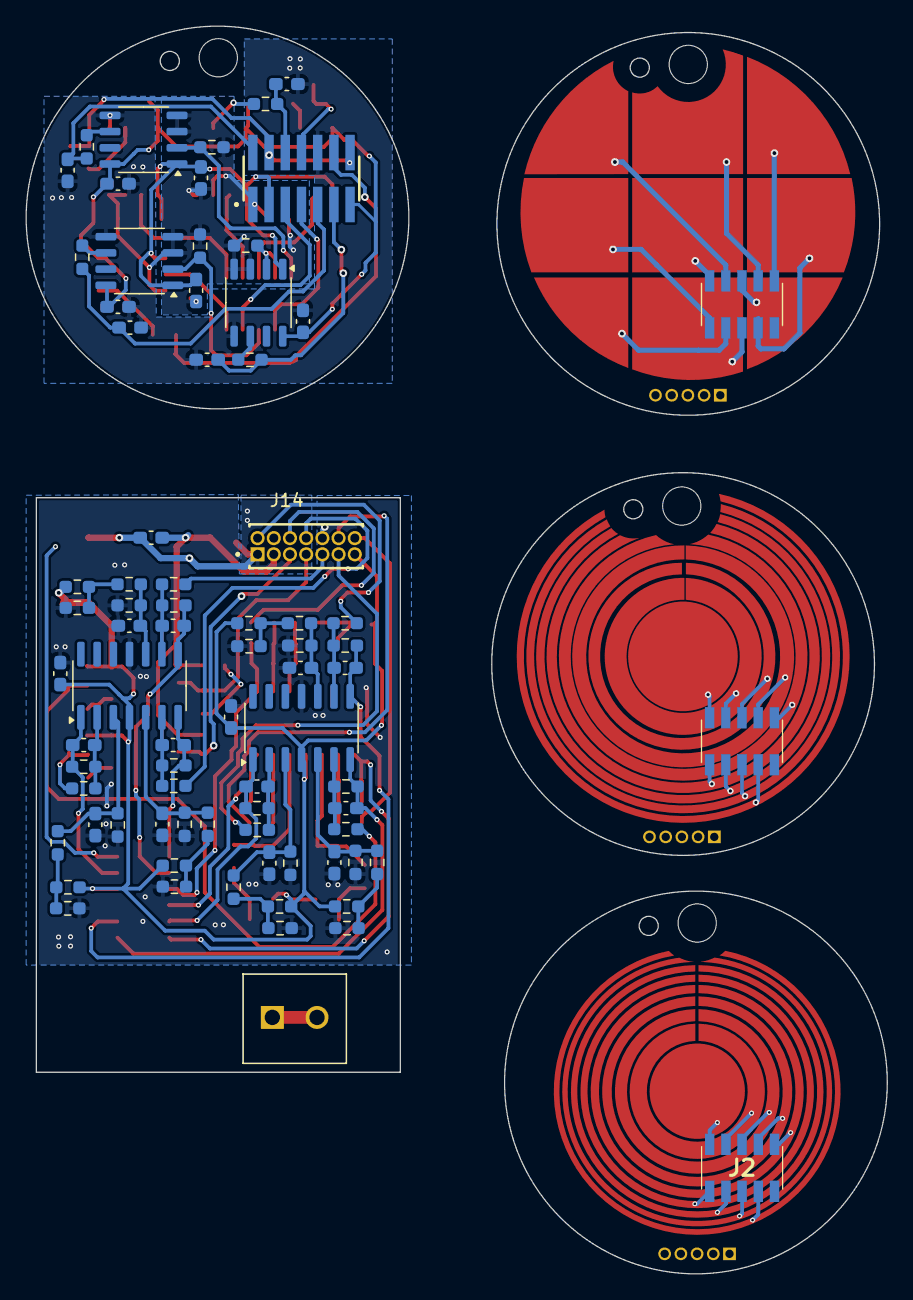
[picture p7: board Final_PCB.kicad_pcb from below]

Board: 2 copper layers, 67.5 x 97.8 mm, 143 parts (78 on the bottom side), 68 nets.

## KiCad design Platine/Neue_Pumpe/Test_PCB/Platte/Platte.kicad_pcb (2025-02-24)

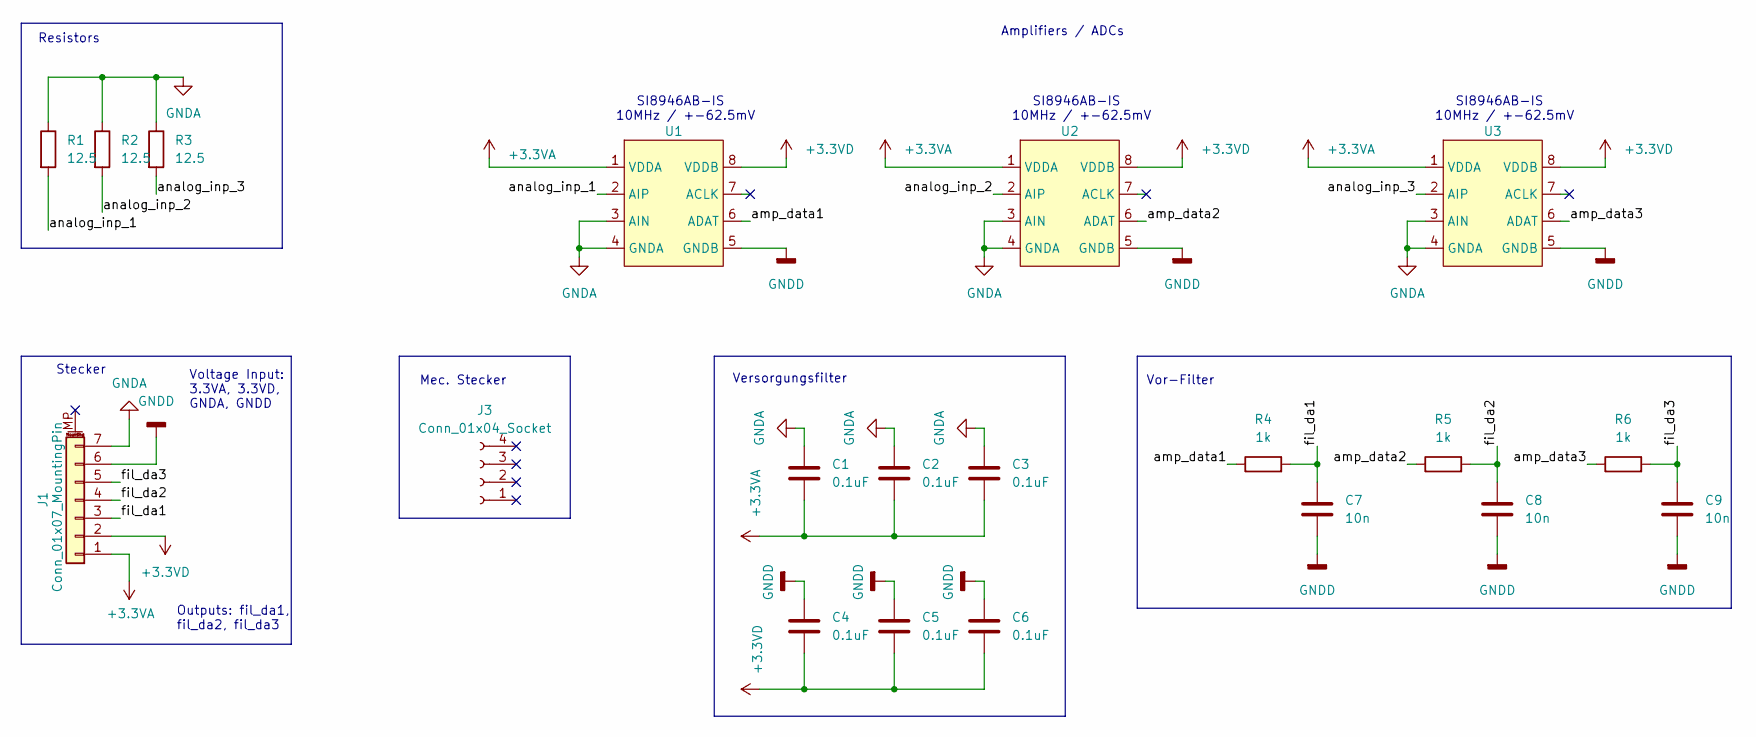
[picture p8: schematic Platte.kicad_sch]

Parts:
C1, C2, C3, C4, C5, C6: 0.1uF; C_0603_1608Metric_Pad1.08x0.95mm_HandSolder
C7, C8, C9: 10n; C_0603_1608Metric_Pad1.08x0.95mm_HandSolder
J1: Conn_01x07_MountingPin; JST_GH_BM07B-GHS-TBT_1x07-1MP_P1.25mm_Vertical
J3: Conn_01x04_Socket; PinHeader_1x04_P1.27mm_Vertical
R1, R2, R3: 12.5; R_0603_1608Metric_Pad0.98x0.95mm_HandSolder
R4, R5, R6: 1k; R_0603_1608Metric_Pad0.98x0.95mm_HandSolder
U1, U2, U3: SOP-8_3.9x4.9mm_P1.27mm

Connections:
+3.3VA: C1.2, C2.2, C3.2, J1.1, U1.1 (VDDA), U2.1 (VDDA), U3.1 (VDDA)
+3.3VD: C4.2, C5.2, C6.2, J1.2, U1.8 (VDDB), U2.8 (VDDB), U3.8 (VDDB)
/amp_data1: R4.1, U1.6 (ADAT)
/amp_data2: R5.1, U2.6 (ADAT)
/amp_data3: R6.1, U3.6 (ADAT)
/analog_inp_1: R1.2, U1.2 (AIP)
/analog_inp_2: R2.2, U2.2 (AIP)
/analog_inp_3: R3.2, U3.2 (AIP)
/fil_da1: C7.1, J1.3, R4.2
/fil_da2: C8.1, J1.4, R5.2
/fil_da3: C9.1, J1.5, R6.2
GNDA: C1.1, C2.1, C3.1, J1.7, R1.1, R2.1, R3.1, U1.3 (AIN), U1.4 (GNDA), U2.3 (AIN), U2.4 (GNDA), U3.3 (AIN), U3.4 (GNDA)
GNDD: C4.1, C5.1, C6.1, C7.2, C8.2, C9.2, J1.6, U1.5 (GNDB), U2.5 (GNDB), U3.5 (GNDB)

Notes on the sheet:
SI8946AB-IS 10MHz / +-62.5mV
Resistors
Mec. Stecker
Stecker
Versorgungsfilter
Outputs: fil_da1, fil_da2, fil_da3
Amplifiers / ADCs
Voltage Input: 3.3VA, 3.3VD, GNDA, GNDD
Vor-Filter

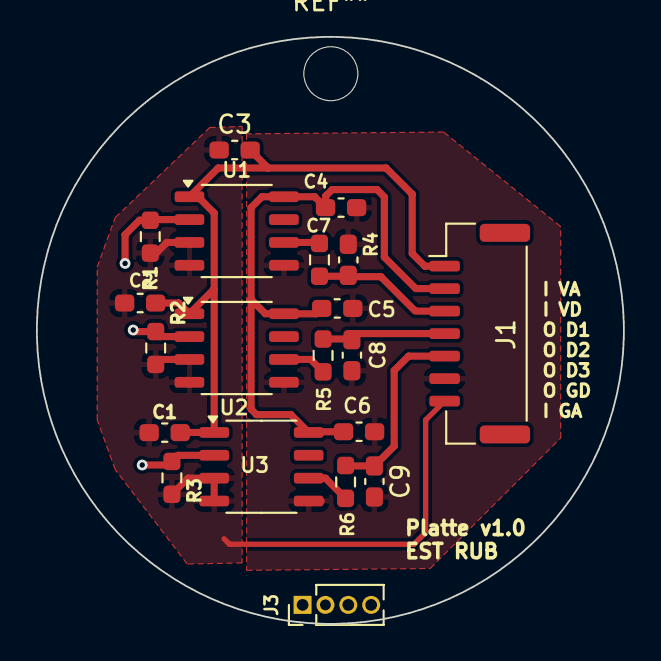
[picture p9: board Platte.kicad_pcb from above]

Board: 2 copper layers, 32.6 x 32.6 mm, 20 parts (0 on the bottom side), 13 nets.

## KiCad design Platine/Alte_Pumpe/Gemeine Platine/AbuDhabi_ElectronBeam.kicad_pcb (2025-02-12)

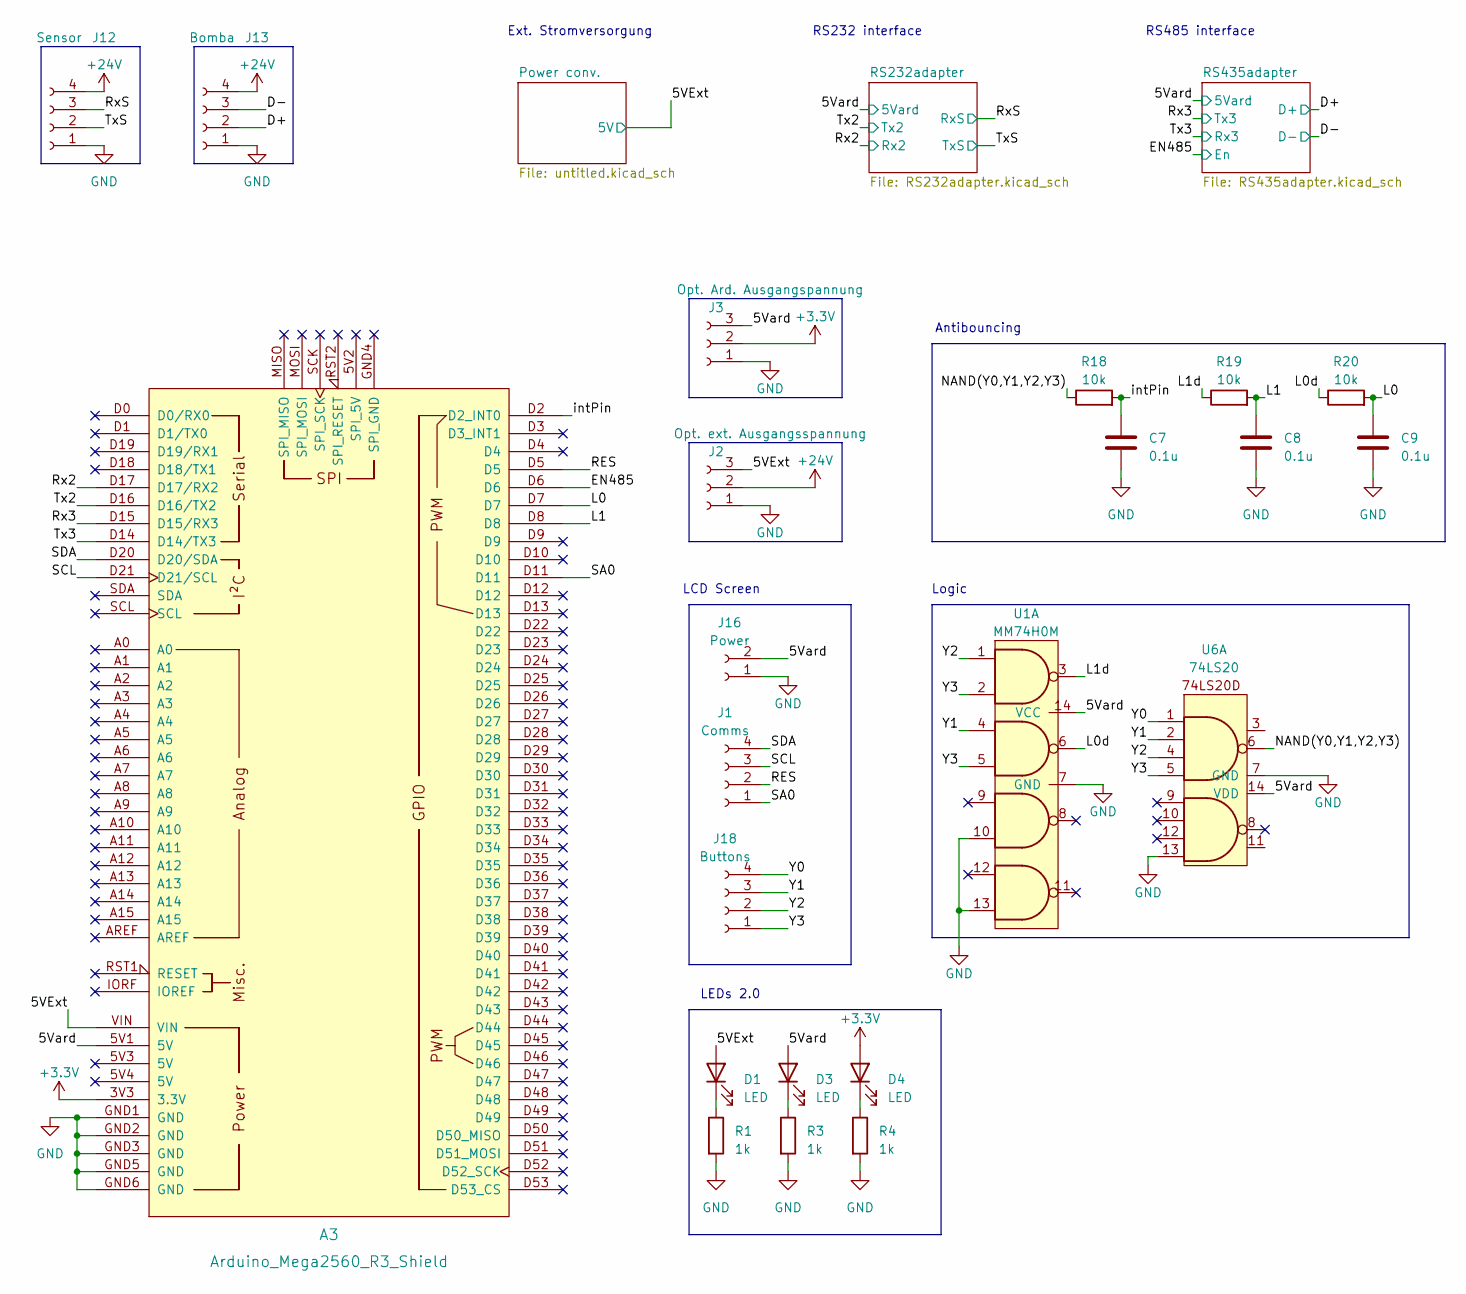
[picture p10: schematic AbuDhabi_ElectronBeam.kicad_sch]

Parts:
A3: Arduino_Mega2560_R3_Shield
C7, C8, C9: 0.1u; C_0603_1608Metric
D1, D3, D4: LED; LED_0603_1608Metric_Pad1.05x0.95mm_HandSolder
J1: Comms; PinSocket_1x04_P2.54mm_Vertical
J2: Opt. ext. Ausgangsspannung; PinSocket_1x03_P2.54mm_Vertical
J3: Opt. Ard. Ausgangspannung; PinSocket_1x03_P2.54mm_Vertical
J12: Sensor; JST_EH_B4B-EH-A_1x04_P2.50mm_Vertical
J13: Bomba; JST_EH_B4B-EH-A_1x04_P2.50mm_Vertical
J16: Power; PinSocket_1x02_P2.54mm_Vertical
J18: Buttons; PinSocket_1x04_P2.54mm_Vertical
R1, R3, R4: 1k; R_0603_1608Metric_Pad0.98x0.95mm_HandSolder
R18, R19, R20: 10k; R_0603_1608Metric
U1: MM74H0M; SOIC-14_3.9x8.7mm_P1.27mm
U6: 74LS20; SOIC-14_3.9x8.7mm_P1.27mm

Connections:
+3.3V: A3.3V3 (3.3V), D4.2 (A), J3.2
/5Vard: A3.5V1 (5V), D3.2 (A), J3.3, J16.2, U1.14 (VCC), U6.14 (VDD); also elsewhere on the board
/D+: J13.2; also elsewhere on the board
/D-: J13.3; also elsewhere on the board
/EN485: A3.D6; also elsewhere on the board
/L0: A3.D7, C9.1, R20.2
/L0d: R20.1, U1.6
/L1: A3.D8, C8.1, R19.2
/L1d: R19.1, U1.3
/NAND(Y0,Y1,Y2,Y3): R18.1, U6.6
/RES: A3.D5, J1.2
/Rx2: A3.D17 (D17/RX2); also elsewhere on the board
/Rx3: A3.D15 (D15/RX3); also elsewhere on the board
/RxS: J12.3; also elsewhere on the board
/SA0: A3.D11, J1.1
/SCL: A3.D21 (D21/SCL), J1.3
/SDA: A3.D20 (D20/SDA), J1.4
/Tx2: A3.D16 (D16/TX2); also elsewhere on the board
/Tx3: A3.D14 (D14/TX3); also elsewhere on the board
/TxS: J12.2; also elsewhere on the board
/Y0: J18.4, U6.1
/Y1: J18.3, U1.4, U6.2
/Y2: J18.2, U1.1, U6.4
/Y3: J18.1, U1.2, U1.5, U6.5
/intPin: A3.D2 (D2_INT0), C7.1, R18.2
GND: A3.GND1 (GND), A3.GND2 (GND), A3.GND3 (GND), A3.GND5 (GND), A3.GND6 (GND), C7.2, C8.2, C9.2, J2.1, J3.1, J12.1, J13.1, J16.1, R1.2, R3.2, R4.2, U1.7 (GND), U1.10, U1.13, U6.7 (GND), U6.13; also elsewhere on the board
unnamed: D1.1 (K), R1.1
unnamed: D3.1 (K), R3.1
unnamed: D4.1 (K), R4.1

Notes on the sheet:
Logic
LCD Screen
Ext. Stromversorgung
RS485 interface
Antibouncing
RS232 interface
LEDs 2.0

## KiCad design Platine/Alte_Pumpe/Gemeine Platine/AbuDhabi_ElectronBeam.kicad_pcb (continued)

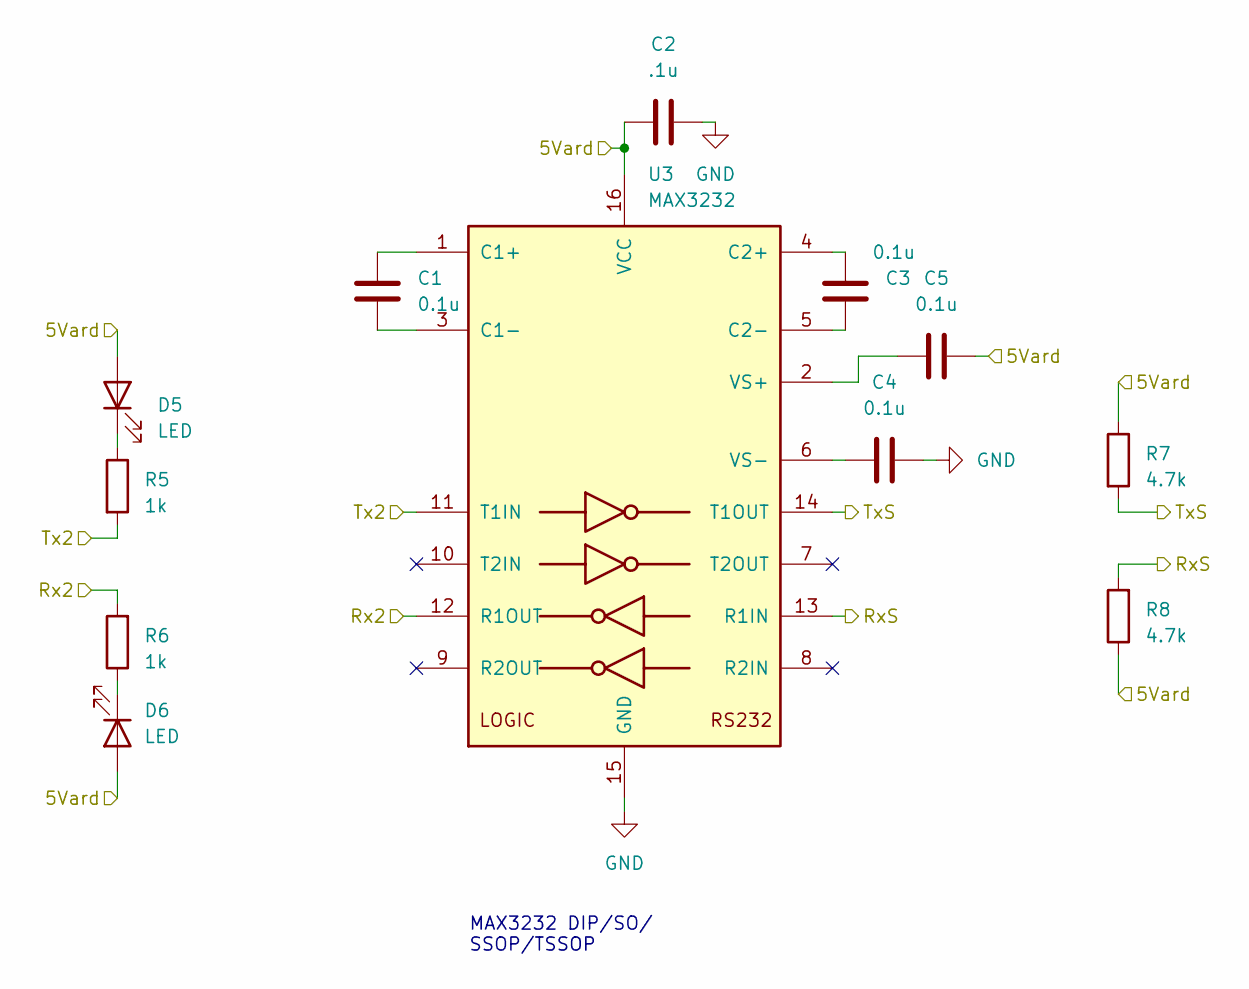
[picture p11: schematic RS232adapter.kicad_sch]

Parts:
C1, C3, C4, C5: 0.1u; C_0603_1608Metric
C2: .1u; C_0603_1608Metric
D5: LED; LED_0603_1608Metric
D6: LED; LED_0603_1608Metric_Pad1.05x0.95mm_HandSolder
R5, R6: 1k; R_0603_1608Metric
R7, R8: 4.7k; R_0603_1608Metric
U3: MAX3232; SOIC-16_3.9x9.9mm_P1.27mm

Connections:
/5Vard: C2.1, C5.2, D5.2 (A), D6.2 (A), R7.1, R8.1, U3.16 (VCC); also elsewhere on the board
/Rx2: R6.2, U3.12 (R1OUT); also elsewhere on the board
/RxS: R8.2, U3.13 (R1IN); also elsewhere on the board
/Tx2: R5.2, U3.11 (T1IN); also elsewhere on the board
/TxS: R7.2, U3.14 (T1OUT); also elsewhere on the board
GND: C2.2, C4.2, U3.15 (GND); also elsewhere on the board
unnamed: D5.1 (K), R5.1
unnamed: D6.1 (K), R6.1
unnamed: C1.1, U3.1 (C1+)
unnamed: C1.2, U3.3 (C1-)
unnamed: C3.1, U3.4 (C2+)
unnamed: C3.2, U3.5 (C2-)
unnamed: C5.1, U3.2 (VS+)
unnamed: C4.1, U3.6 (VS-)

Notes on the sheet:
MAX3232 DIP/SO/ SSOP/TSSOP

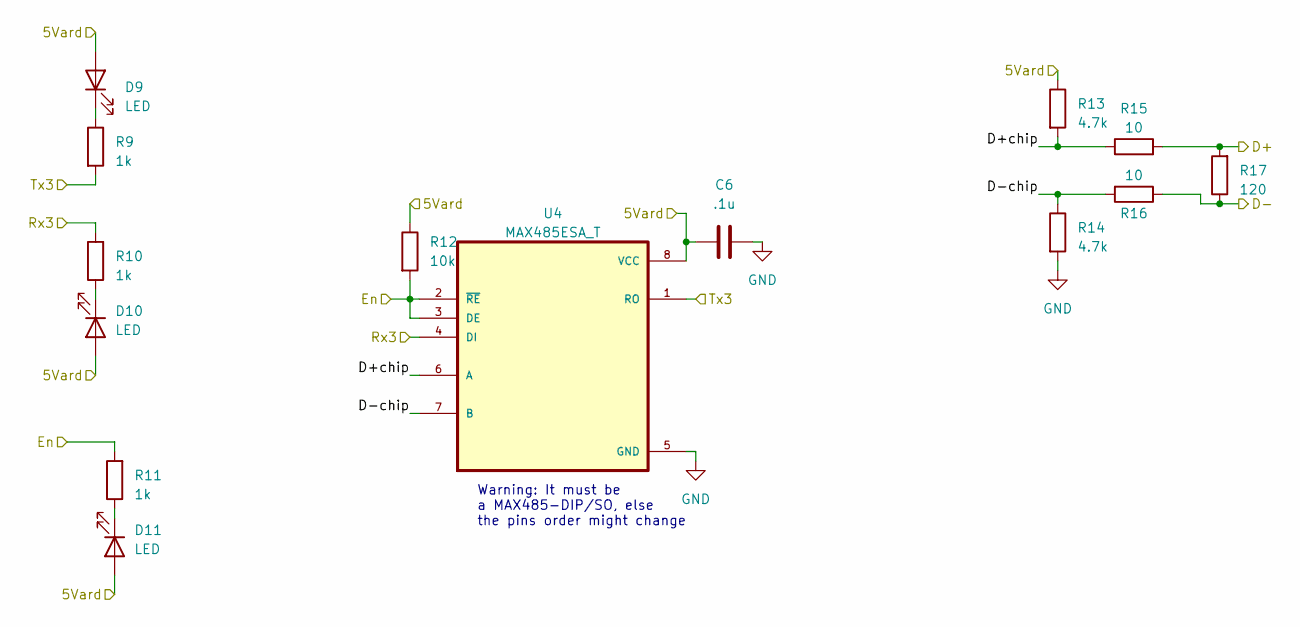
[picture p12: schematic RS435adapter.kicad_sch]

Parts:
C6: .1u; C_0603_1608Metric
D9, D10, D11: LED; LED_0603_1608Metric
R9, R10, R11: 1k; R_0603_1608Metric
R12: 10k; R_0603_1608Metric
R13, R14: 4.7k; R_0603_1608Metric
R15, R16: 10; R_0603_1608Metric
R17: 120; R_0603_1608Metric
U4: MAX485ESA_T; SOIC127P600X175-8N

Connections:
/5Vard: C6.1, D9.2 (A), D10.2 (A), D11.2 (A), R12.1, R13.1, U4.8 (VCC); also elsewhere on the board
/D+: R15.2, R17.2; also elsewhere on the board
/D-: R16.1, R17.1; also elsewhere on the board
/EN485: R11.2, R12.2, U4.2 (~RE), U4.3 (DE); also elsewhere on the board
/RS435adapter/D+chip: R13.2, R15.1, U4.6 (A)
/RS435adapter/D-chip: R14.1, R16.2, U4.7 (B)
/Rx3: R9.2, U4.1 (RO); also elsewhere on the board
/Tx3: R10.2, U4.4 (DI); also elsewhere on the board
GND: C6.2, R14.2, U4.5 (GND); also elsewhere on the board
unnamed: D9.1 (K), R9.1
unnamed: D10.1 (K), R10.1
unnamed: D11.1 (K), R11.1

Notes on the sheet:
Warning: It must be a MAX485-DIP/SO, else the pins order might change

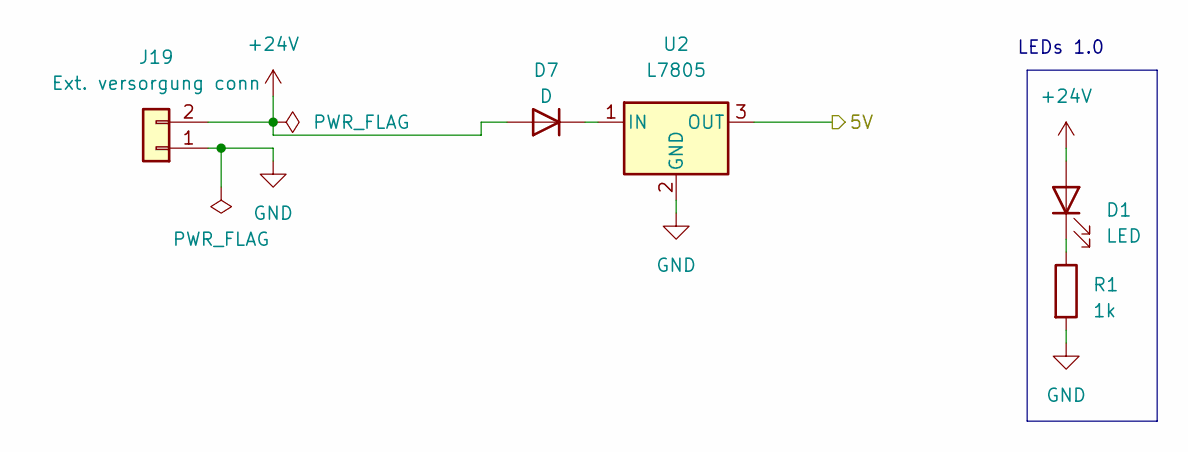
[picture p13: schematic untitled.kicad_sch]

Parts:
D1: LED; LED_0603_1608Metric_Pad1.05x0.95mm_HandSolder
D7: D; LED_0603_1608Metric_Pad1.05x0.95mm_HandSolder
J19: Ext. versorgung conn; JST_EH_B2B-EH-A_1x02_P2.50mm_Vertical
R1: 1k; R_0603_1608Metric
U2: L7805; TO-220-3_Vertical

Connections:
GND: J19.1, R1.2, U2.2 (GND); also elsewhere on the board
unnamed: D1.1 (K), R1.1
unnamed: D7.1 (K), U2.1 (IN)

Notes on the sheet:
LEDs 1.0

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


Board: 2 copper layers, 130.0 x 145.0 mm, 53 parts (11 on the bottom side), 46 nets.

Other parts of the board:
D2: LED; LED_0603_1608Metric_Pad1.05x0.95mm_HandSolder
R2: 1k; R_0603_1608Metric

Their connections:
GND: R2.2; also elsewhere on the board
unnamed: D2.1 (K), R2.1

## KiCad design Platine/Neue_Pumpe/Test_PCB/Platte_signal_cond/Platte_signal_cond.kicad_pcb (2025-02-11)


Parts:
C1, C2, C3, C4, C5, C6: 100p; C_0603_1608Metric_Pad1.08x0.95mm_HandSolder
C7, C8: 10u; C_0603_1608Metric_Pad1.08x0.95mm_HandSolder
C9: 100n; C_0603_1608Metric_Pad1.08x0.95mm_HandSolder
J1: Conn_01x06; JST_EH_B6B-EH-A_1x06_P2.50mm_Vertical
J2: Conn_01x07_MountingPin; JST_GH_BM07B-GHS-TBT_1x07-1MP_P1.25mm_Vertical
R1, R7, R11, R12, R17, R18: 252k; R_0603_1608Metric_Pad0.98x0.95mm_HandSolder
R2, R4, R9, R10, R15, R16: 100k; R_0603_1608Metric_Pad0.98x0.95mm_HandSolder
R3, R5, R6, R8, R13, R14: 1k; R_0603_1608Metric_Pad0.98x0.95mm_HandSolder
U1: SMDIP-8_W9.53mm
U2: SOIC-14_3.9x8.7mm_P1.27mm

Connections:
+3.3VA: C8.2, J2.4, U1.5 (+Vout)
+3.3VD: C7.2, C9.2, J1.3, J2.3, R3.1, R6.1, R13.1, U1.2 (+Vin), U2.4 (V+)
/Out1: C4.1, J1.5, R7.2, U2.1 (OUT1)
/Out2: C3.1, J1.4, R12.2, U2.7 (OUT2)
/Out3: C6.1, J1.6, R18.2, U2.8 (OUT3)
/Vin1+: C1.2, R1.1, R2.1, U2.3 (IN1+)
/Vin1-: C4.2, R4.1, R7.1, U2.2 (IN1-)
/Vin2+: C2.2, R9.1, R11.1, U2.5 (IN2+)
/Vin2-: C3.2, R10.1, R12.1, U2.6 (IN2-)
/Vin3+: C5.2, R15.1, R17.1, U2.10 (IN3+)
/Vin3-: C6.2, R16.1, R18.1, U2.9 (IN3-)
/data_in1: J2.6, R4.2
/data_in2: J2.7, R10.2
/data_in3: J2.5, R16.2
GNDA: C8.1, J1.2, J2.2, U1.4 (-Vout)
GNDD: C1.1, C2.1, C5.1, C7.1, C9.1, J1.1, J2.1, R1.2, R5.2, R8.2, R11.2, R14.2, R17.2, U1.1 (-Vin), U2.11 (V-)
unnamed: R2.2, R3.2, R5.1
unnamed: R6.2, R8.1, R9.2
unnamed: R13.2, R14.1, R15.2

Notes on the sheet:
kommt aus Draußen: 3.3VD, GNDD, VPlatte drinnen: 3.3VA, GNDA
Cut frequency: 25 kHz Voltage gain: 2.5
DC/DC isolated Wandler
TLV9004QDRQ1
Op Amps
Stecker (zw. Sign. cond. Platine und Platte-Platine)
NTE0303MC
Stecker (von draußen)



Board: 2 copper layers, 35.8 x 32.5 mm, 35 parts (3 on the bottom side), 19 nets.

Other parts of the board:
M1, M2, M3, M4: MountingHole_2.1mm

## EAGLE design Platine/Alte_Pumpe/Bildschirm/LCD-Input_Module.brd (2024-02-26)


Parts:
C1, C2, C3, C4, C5, C6, C7: 1u; C0603
JP1: PINHD-1X2; 1X02
JP2: PINHD-1X4; 1X04
R5: 24; R0603
R6: 18; R0603
R7, R8: R-EU_R0603; R0603
U$1: DOGM204-A; LCD

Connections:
!RES: JP2.3, U$1.P$44 (!RESET)
GND: C1.2, C2.2, C3.2, C4.2, C5.2, C6.2, C7.2, JP1.2, R5.1, R6.1, U$1.P$29 (IM2), U$1.P$30 (IM1), U$1.P$32 (VSS); also elsewhere on the board
unnamed: C3.1, U$1.P$24 (V0)
unnamed: C6.1, U$1.P$27 (V3)
unnamed: C4.1, U$1.P$25 (V1)
unnamed: C5.1, U$1.P$26 (V2)
unnamed: C7.1, U$1.P$28 (V4)
unnamed: C2.1, U$1.P$23 (VOUT)
unnamed: R5.2, U$1.P$21 (CG)
unnamed: R6.2, U$1.P$22 (CR)
SA0: JP2.4, U$1.P$43 (RS)
SCL: JP2.2, R8.2, U$1.P$40 (D0)
SDA: JP2.1, R7.2, U$1.P$38 (D2), U$1.P$39 (D1)
VDD: C1.1, JP1.1, R7.1, R8.1, U$1.P$1 (AGR), U$1.P$31 (VDD), U$1.P$33 (D7), U$1.P$34 (D6), U$1.P$35 (D5), U$1.P$36 (D4), U$1.P$37 (D3), U$1.P$41 (E), U$1.P$42 (R/!W); also elsewhere on the board


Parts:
JP3: PINHD-1X4; 1X04
R1, R2, R3, R4: R-EU_R0603; R0603
S1-UP, S2-DOWN, S3-OK, S4-CAN: PTS647; PTS647-TACTSWITCH

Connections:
CANCEL: JP3.4, R4.1, S4-CAN.3 (2), S4-CAN.4 (2)
DOWN: JP3.2, R2.1, S2-DOWN.3 (2), S2-DOWN.4 (2)
GND: S1-UP.1, S1-UP.2 (1), S2-DOWN.1, S2-DOWN.2 (1), S3-OK.1, S3-OK.2 (1), S4-CAN.1, S4-CAN.2 (1); also elsewhere on the board
OK: JP3.3, R3.1, S3-OK.3 (2), S3-OK.4 (2)
UP: JP3.1, R1.1, S1-UP.3 (2), S1-UP.4 (2)
VDD: R1.2, R2.2, R3.2, R4.2; also elsewhere on the board



Board: 2 copper layers, 100.0 x 65.0 mm, 23 parts (20 on the bottom side), 18 nets.

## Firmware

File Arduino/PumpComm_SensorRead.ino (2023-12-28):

#define READ 0
#define WRITE 1
#define PARAMSIZE 4

// Arduino pins
const int ENRS485Pin = 2; //RS-485 shield enable terminal, on arduino uno it would be digital port 2 using DFROBOT shield

const char endChar = '\r';  // ASCII character 13
// Setting Parameters
const char ErrorAckn[PARAMSIZE] = "009";
const char PumpgnStatn[PARAMSIZE] = "010";
const char CfgSpdSwPt[PARAMSIZE] = "017";
const char MotorPump[PARAMSIZE] = "023";
const char OpModeBKP[PARAMSIZE] = "025";
const char SpdSetMode[PARAMSIZE] = "026";
const char GasMode[PARAMSIZE] = "027";
const char CfgAccA1[PARAMSIZE] = "035";
const char CfgAccA2[PARAMSIZE] = "036";

// Status only
const char ErrorCode[PARAMSIZE] = "303";
const char SetRotSpd[PARAMSIZE] = "308";
const char ActualSpd[PARAMSIZE] = "309";
const char NominalSpd[PARAMSIZE] = "315"; //HiPace 10 -> 1500 Hz = 1.5kHz
const char TempElec[PARAMSIZE] = "326";
const char TempPmpBot[PARAMSIZE] = "330";
const char TempBearng[PARAMSIZE] = "342";
const char Pressure[PARAMSIZE] = "340";
const char TempMotor[PARAMSIZE] = "346";

// Sollwertvorgaben
const char SpdSwtPt1[PARAMSIZE] = "701"; 
const char SpdSVal[PARAMSIZE] = "707";
const char SpdSwtPt2[PARAMSIZE] = "719";
const char PrsSn1Name[PARAMSIZE] = "739";
const char Pressure1[PARAMSIZE] = "740"; // Atm. pressure at 100m aboce level of the sea ~ 990mbar
const char PrsCorriPi1[PARAMSIZE] = "742";

const int boolDataType = 0;
const int intLongDataType = 1;
const int intRealDataType = 2;
const int stringDataType = 4;
const int intShortDataType = 7;
const int expoDataType = 10;
const int requestData = 13;

const int paramCommSize = 10;
const int commandSize = 20; // Every command in RS485 protocol has 10 character to specify what type of request/command 
                            // the master requires from the slave. I'll assume that the maximum data size will be 06, 
                            // which means that total command size is 20

char outCommand[commandSize] = {0};
char command[commandSize] = {0};
char answer[commandSize+1] = {0};
char paramStr[PARAMSIZE] = {0};

char debugInput;

bool changeStatus = false;
bool MotorPumpStatus = false;
bool BackPumpStatus = false;
bool ShowAnswer = false;

bool setupVar = true;

//Interval variables and values: this code doesn't use any delay function. to allow the use of interruptions and events for debugging
//Instead, everything is set in different interval of time trying to avoid any collition on the different communication functions
const unsigned long checkInterval = 3000;
unsigned long lastCheckMillis = 0;
const unsigned long checkPressureInterval = 2000;
unsigned long lastCheckPressureMillis = 0;
const unsigned long setupInterval = 500;
unsigned long lastSetupMillis = 0;
const unsigned long ReadInterval = 17; //RS485 specification
unsigned long lastReadMillis = 0;
const unsigned long ReceivedRS232Interval = 20; //RS232 specification
unsigned long lastReceivedRS232Millis = 0;

int queryTurn = 0;

// Stored variables, from DCU comunication
char SensorName[7];
double PressRPTData = 0.0;
int ElecTemp = 0;

// Pressure sensor variables
byte receivedData[9]={0}; 
double PressureValue = 0.0;
byte highByte;
byte lowByte;

// Interval managing variables for pressure sensor
const int PresSenInterval = 100;
unsigned long PreviousPresSenMillis = 0;

void setup() {
  Serial.begin(9600); // debugging
  Serial3.begin(9600, SERIAL_8N1); //TX3RX3 - Serial port used to interface with the RS-232 communication protocol
  Serial2.begin(9600); //TX2RX2 - Serial port used to interface with the RS-485 communication protocol

  // RS485 Communication control pins
  pinMode(ENRS485Pin, OUTPUT);

  RS485Mode(READ);
}

void loop() {
  if(setupVar == true){
    if(millis() - lastSetupMillis >= setupInterval){ 
      RS485Mode(WRITE);

      if(queryTurn == 0){
        Serial.println("Pumping station: ");
        instructConst(1, WRITE, PumpgnStatn, 6, boolDataType, 1, command);
        queryTurn++;
      }else if(queryTurn == 1){
        Serial.println("Config Accessor A1: ");
        instructConst(1, WRITE, CfgAccA1, 3, intShortDataType, 3, command);
        queryTurn++;
      }else if(queryTurn == 2){
        Serial.println("Config Accessor B1: ");
        instructConst(1, WRITE, CfgAccA2, 3, intShortDataType, 6, command);
        queryTurn++;
      }else if(queryTurn == 3){
        Serial.println("Gas Mode: ");
        instructConst(1, WRITE, GasMode, 3, intShortDataType, 1, command);
        queryTurn++;
      }else if(queryTurn == 4){
        Serial.println("Operation Mode Backing Pump: ");
        instructConst(1, WRITE, OpModeBKP, 3, intShortDataType, 2, command);
        queryTurn++;
      }else if(queryTurn == 5){
        Serial.println("PV.can attached sensor name:");
        instructConst(1, READ, PrsSn1Name, 2, requestData, 0, command);
        queryTurn++;
      }else if(queryTurn == 6){
        Serial.println("Pressure sensor calibration factor:");
        instructConst(1, WRITE, PrsCorriPi1, 6, intRealDataType, (int)1.0*100, command);
        queryTurn++;
      }else if(queryTurn == 7){
        Serial.println("Motor turbo Pump: ");
        instructConst(1, WRITE, MotorPump, 6, boolDataType, 0, command);
        queryTurn = 0;
        setupVar = false;
      }
      
      Serial2.write(command);
      Serial2.write(endChar);
      Serial2.flush();

      memset(command, 0, sizeof(command));
      
      lastSetupMillis += setupInterval;
    }
    
  }else if(setupVar == false){
    if(millis() - lastCheckMillis >= checkInterval){ 
      RS485Mode(WRITE);
          
      if(queryTurn == 0){ 
        instructConst(1, READ, ActualSpd, 2, requestData, 0, outCommand);
        queryTurn++;
      }else if(queryTurn == 1){
        instructConst(1, READ, TempElec, 2, requestData, 0, outCommand);
        queryTurn++;
      }else if(queryTurn == 2){
        instructConst(1, READ, TempPmpBot, 2, requestData, 0, outCommand);
        queryTurn++;
      }else if(queryTurn == 3){
        instructConst(1, READ, ErrorCode, 2, requestData, 0, outCommand);
        queryTurn = 0;
      }

      Serial2.write(outCommand);
      Serial2.write(endChar);
      Serial2.flush();

      memset(outCommand, 0, sizeof(outCommand));

      lastCheckMillis += checkInterval;
    }
    
    if(millis() - lastCheckPressureMillis >= checkPressureInterval){ 
      RS485Mode(WRITE);

      instructConst(1, READ, Pressure1, 2, requestData, 0, command);
      Serial.print("ITR 090: ");
      Serial.print(PressureValue, 4);  
      Serial.println(" mbar");

      Serial2.write(command);
      Serial2.write(endChar);
      Serial2.flush();

      memset(command, 0, sizeof(command));

      lastCheckPressureMillis += checkPressureInterval;
    }

  }

  if(millis() - lastReadMillis >= ReadInterval){
    ReadRS485Serial(answer);
    if(ShowAnswer) {
      SaveAnswer();
      ShowAnswer = false;
    }
    
    lastReadMillis += ReadInterval;
  }
    
  ReadPressure();
}

//================================================================== FUNCTIONS ======================================================

// This is only a helper to allow ease in reading the code, because of the shield that is being used, the connection of DE an !RE is 
// done analogical, yet for the IC that is not a certainty  
void RS485Mode(bool mode){
  digitalWrite(ENRS485Pin, mode);
}

// This function works to partially automatize the constrcution of the outgoing command, the idea is to generalize the funtion either 
// using a configuration file or a dictionary with the important parameters. Rn, it works with almost all types of commands that use
// the DCU, still is not complete.
char instructConst(int address, bool mode, char param[], const int dataLength, const int dataType,
                  int inData, char str[]){
  char i[4];
  itoa(address, i, 10);
  if(address<10){
    strcpy(str, "00");
    strcat(str, i);
  }else if(address >= 10 && address < 100){
    strcpy(str, "0");
    strcat(str, i);
  }else strcpy(str, i);

  if(mode) strcat(str, "10");
  else strcat(str, "00");

  strcat(str, param);
  
  itoa(dataLength, i, 10);

  if(dataLength < 10){
    strcat(str, "0");
    strcat(str, i);
    
  }else strcat(str, i);
  
  if(dataLength == 2) strcat(str, "=?");
    
  else if(dataType == boolDataType){
    if(inData == 1) strcat(str, "111111");
    else if(inData == 0) strcat(str, "000000");

  }else if((dataType == intLongDataType)|| (dataType == intRealDataType)){
    char data[dataLength];
    itoa(inData, data, 10);

    if(inData < 10){
      strcat(str, "00000");
      strcat(str, data);
      
    }else if(inData >= 10 && inData < 100){
      strcat(str, "0000");
      strcat(str, data);
      
    }else if(inData >= 100 && inData < 1000){
      strcat(str, "000");
      strcat(str, data);
      
    }else if(inData >= 1000 && inData < 10000){
      strcat(str, "00");
      strcat(str, data);
      
    }else if(inData >= 10000 && inData < 100000){
      strcat(str, "0");
      strcat(str, data);
      
    }else strcat(str, data);

  }else if(dataType == intShortDataType){
    char data[dataLength];
    itoa(inData, data, 10);
    
    if(inData < 10){
      strcat(str, "00");
      strcat(str, data);
      
    }else if(inData >= 10 && inData < 100){
      strcat(str, "0");
      strcat(str, data);
      
    }else strcat(str, data);
  }

  char Check[4];
  int checkSum = ASCIIsum(0, paramCommSize + dataLength - 1, str) % 256;
  itoa(checkSum, Check, 10);
  if(checkSum <10){
    strcat(str, "00");
    strcat(str, Check);
  }else if(checkSum>=10 && checkSum<100){
    strcat(str, "0");
    strcat(str, Check);
  }else strcat(str, Check);

  return str;
}

char ReadRS485Serial(char strAnswer[]){
  RS485Mode(READ);
  if(Serial2.available()){
    static int i = 0;
    char ch = Serial2.read();
    if(ch != endChar && i < commandSize-1){
      strAnswer[i] = ch;
      i++;
    }else if(ch == endChar || i == commandSize-1){
      while(i < commandSize){
        if(i == commandSize-1){
          i = 0;
          ShowAnswer = true;
          break;
        }
        strAnswer[i] = '\0'; // null terminator character, in string it signifies the end of a string (null-terminated string)
        i++;
      }
    }
  }
  return strAnswer;
}
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

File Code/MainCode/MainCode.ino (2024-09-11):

<<<<<<< HEAD
#include "PfeifferTC110.h"
#include <Arduino.h>
#include <SSD1803A_I2C.h>
#include<wire.h>
#include "SensorRS232Comm.h"

TwoWire Wire1;

// Arduino pins
const int ENRS485Pin = 6;

TC110 turboPump(byte(ENRS485Pin), Serial3);

char command[COMMANDSIZE] = {0};
char outCommand[COMMANDSIZE] = {0};
char answer[COMMANDSIZE+1] = {0};
char paramStr[PARAMSIZE] = {0};

char debugInput;

bool changeStatus = false;
bool MotorPumpStatus = false;
bool BackPumpStatus = false;

bool setupVar = true;

double PressureValue = 0.0; // ITR090 Pressure
ITR090 pressSensor(Serial2);


const unsigned long checkInterval = 3000;
unsigned long lastCheckMillis = 0;
const unsigned long checkPressureInterval = 2000;
unsigned long lastCheckPressureMillis = 0;
const unsigned long setupInterval = 500;
unsigned long lastSetupMillis = 0;
const unsigned long ReadInterval = 17;
unsigned long lastReadMillis = 0;

int queryTurn = 0;

// ================================= SCREEN ================================

const uint8_t i2cAddr = 0x3D;
const uint8_t resetPin = 5;
const uint8_t address_pin = 11;

// Interruption settings
const byte interruptPin = 2;
const byte L0pin=7;
const byte L1pin=8;
int L0=0;
int L1=0;

// ***** State machine *****
#define UP 0
#define DOWN 1
#define OK 2
#define CANCEL 3
int arrow_state=0; // arrow position
int last_arrow_state=3; // highest possible arrow position
int screen_state=0;
bool int_1_activated=false; // Screen state
bool int_2_activated=false; // Arrow state
int pressed_button=UP;
int change_state_flag=2; // 2 means no state should be changed
int changeStateMillis=0;
int changeStateInterval=25;

uint8_t SelectArrow[8] = {
  0b00000,
  0b00100,
  0b01100,
  0b11111,
  0b11111,
  0b01100,
  0b00100,
  0b00000
  };
uint8_t degree[8] = {
  0b00111,
  0b00101,
  0b00111,
  0b00000,
  0b00000,
  0b00000,
  0b00000,
  0b00000
  };


bool reset = HIGH;

SSD1803A_I2C lcd(i2cAddr, resetPin);
int arrow_state_test=0;

void setup() {
  turboPump.init();
  pressSensor.init();
  Serial.begin(9600); // debugging

  pinMode(address_pin, OUTPUT);
  digitalWrite(address_pin, HIGH);
  pinMode(resetPin, OUTPUT);
  digitalWrite(resetPin, reset);
  lcd.begin(Wire1, DOGM204); 
  lcd.display(SET_ROM_B);

  lcd.create(0, SelectArrow);
  lcd.create(1, degree);

  // Interruption settings
  pinMode(interruptPin, INPUT);
  pinMode(L0pin, INPUT);
  pinMode(L1pin, INPUT);
  attachInterrupt(digitalPinToInterrupt(interruptPin), interruption, RISING);
}

void loop() {
  PressureValue = pressSensor.readPressure(); // ITR090 read 
  if(setupVar == true){
    if(millis() - lastSetupMillis >= setupInterval){ 
      turboPump.RS485Mode(WRITE);

      if(queryTurn == 0){
        Serial.println("Pumping station: ");
        instructConst(1, WRITE, param["PumpngStatn"], 1, command);
        queryTurn++;

      }else if(queryTurn == 1){
        Serial.println("Config Accessor A1: ");
        instructConst(1, WRITE, param["CfgAccA1"], 3, command);
        queryTurn++;

      }else if(queryTurn == 2){
        Serial.println("Config Accessor B1: ");
        instructConst(1, WRITE, param["CfgAccB1"], 6, command);
        queryTurn++;

      }else if(queryTurn == 3){
        Serial.println("Gas Mode: ");
        instructConst(1, WRITE, param["GasMode"], 1, command);
        queryTurn++;

      }else if(queryTurn == 4){
        Serial.println("Operation Mode Backing Pump: ");
        instructConst(1, WRITE, param["OpModeBKP"], 2, command);
        queryTurn++;

      }else if(queryTurn == 5){
        Serial.println("PV.can attached sensor name:");
        instructConst(1, READ, param["PrsSn1Name"], 0, command);
        queryTurn++;

      }else if(queryTurn == 6){
        Serial.println("Pressure sensor calibration factor:");
        instructConst(1, WRITE, param["PrsCorriP1"], (int)1.0*100, command);
        queryTurn++;
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

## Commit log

2023-12-28 Create README.md
    general description of the arduino program.
    For now, the program is not divided into libraries and it will be uploaded in function parts and UI parts.
2023-12-28 Create PumpComm_SensorRead.ino
    General program of the functionality of the control unit. Here it is a block of code, the idea is to separate it into libraries.
2024-01-15 Create PumpScreenUI.ino
    First functions of the screen UI. This is a display of the data acquire from the pump comm and the sensor.
2024-01-15 Changing screen arduino code so it works with the board
2024-02-16 Create the library for the pressure sensor ITR090 - RS232Comm protocol
2024-02-26 Ergänzung der Projekte der Platinen.
    [AbuDhabi_ElectronBeam-B_Cu.gbr, AbuDhabi_ElectronBeam-B_Mask.gbr, AbuDhabi_ElectronBeam-B_Silkscreen.gbr, AbuDhabi_ElectronBeam-Edge_Cuts.gbr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]
2024-02-26 Small change in schematic
    [AbuDhabi_ElectronBeam.kicad_sch]
2024-03-06 DCU library / turbo pump library done. requires testing. compiles without errors or warnings
2024-03-08 Delete Arduino/PumpComm_SensorRead directory
    to allow commit
2024-03-25 Adding comments to sensor ITR 90 library
2024-03-25 Code fixed so it reads correctly the ITR90 sensor
2024-03-26 adding function to turn on/off the pumps through the lcd screen
2024-04-22 Finished screens in python, now arranging char array from arduino to python
2024-06-18 added command to indicate the ITR090 sensor that the pressure units are mbar
2024-09-11 Viel hat geändert
    [Current_messung.kicad_pcb, Current_messung.kicad_sch, LCD-Input_Module.brd, LCD-Input_Module.sch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]
2024-09-18 Adding a CST simulation
    [Grid_1.stl, Model.dsn, Model.psm, Platte_1.stl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]
2024-09-18 Adding CST simulation with filled cylinder
    [Grid_1.stl, Model.dsn, Model.psm, Platte_1.stl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]
2024-09-18 Adding Hohlzylinider CST simulation
    [Grid_1.stl, Model.dsn, Model.psm, Platte_1.stl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]
2024-09-20 Uploading PCB of the current measuring plate
    [Platte.kicad_pcb, Platte.kicad_sch]
2024-09-23 Changes to plate PCB
    [Platte.kicad_pcb]
2024-09-23 Plate PCB almost done
    [Platte.kicad_pcb, Platte.kicad_sch]
2024-09-25 Few changes plate PCB
    [Platte.kicad_sch]
2024-09-25 small changes
    [Platte.kicad_pcb, Platte.kicad_sch]
2024-09-25 Adding now RC filter and DC Converter to Plate PCB
    [Platte.kicad_sch]
2024-09-30 Nothing special
    [Platte.kicad_sch, sgnlcond.kicad_sch]
2024-10-01 adding signal conditioning phase to plate PCB
    [sgnlcond.kicad_sch]
2024-10-02 not much
    [sgnlcond.kicad_sch]
2024-10-03 Results of changing the voltage on the plate on README file
2024-10-03 plate pcb almost finished
    [Platte.kicad_sch, sgnlcond.kicad_sch]
2024-10-04 Removing CST simulations because of weight, theyre now in the folder outside the repo
    [Grid_1.stl, Model.dsn, Model.psm, Platte.kicad_pcb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]
2024-10-07 Adding footprints to signal conditioning PCB and placing components
    [Platte_signal_cond.kicad_pcb, Platte_signal_cond.kicad_sch]
2024-10-08 PCBs almost finished
    [Platte.kicad_pcb, Platte_signal_cond.kicad_pcb, Platte_signal_cond.kicad_sch]
2024-10-09 PCBs completely finished
    [Platte.kicad_pcb, Platte_signal_cond.kicad_pcb]
2024-10-09 Mit Robin geredet, ein paar Veränderung gemacht
    [Platte.kicad_pcb, Platte.kicad_sch, Platte_signal_cond.kicad_sch]
2024-10-21 LTSpice simulation done. Changing now schematics and PCB
    [Platte.kicad_pcb, Platte.kicad_sch]
2024-10-21 nicht so viel
    [Platte.kicad_pcb, Platte.kicad_sch]
2024-10-23 PCBs ready
    [Platte.kicad_pcb, Platte.kicad_sch, Platte_signal_cond.kicad_pcb, Platte_signal_cond.kicad_sch]
2024-10-23 Modifying working frequency in LTSpice and adding extra resistor in pcb
    [Platte_signal_cond.kicad_pcb, Platte_signal_cond.kicad_sch]
2024-10-24 mit Robin geredet
    [Platte.kicad_pcb]
2024-10-25 Simulation verändert und fertiggemacht
2024-10-29 Final circuits designed. Plate PCB ready, signal cond PCB still in process
    [Platte.kicad_pcb, Platte.kicad_sch, Platte_signal_cond.kicad_pcb, Platte_signal_cond.kicad_sch]
2024-10-30 Made a few changes to PCBs and schematics
    [Platte.kicad_pcb, Platte.kicad_sch, Platte_signal_cond.kicad_pcb, Platte_signal_cond.kicad_sch]
2024-10-30 Both the PCBs finished
    [Platte_signal_cond.kicad_pcb]
2024-10-31 Small correction. Everything finished
    [Platte.kicad_sch, Platte_signal_cond.kicad_pcb, Platte_signal_cond.kicad_sch]
2024-11-05 Better shaping the Plates on the PCB
    [Nutzen-B_Cu.gbr, Nutzen-B_Mask.gbr, Nutzen-B_Silkscreen.gbr, Nutzen-Edge_Cuts.gbr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]
2024-11-13 Ein paar Änderungen
    [Nutzen.kicad_pcb]
2025-01-31 All the changes until today
    [Platte.kicad_pcb]
2025-02-06 Updated Arduino code for reading test PCB
    [Platte_signal_cond.kicad_sch]
2025-02-11 corrections on platte PCB
    [Platte.kicad_pcb, Platte.kicad_sch, Platte_signal_cond.kicad_pcb]
2025-02-12 Starting with final PCB
    [AbuDhabi_ElectronBeam-B_Cu.gbr, AbuDhabi_ElectronBeam-B_Mask.gbr, AbuDhabi_ElectronBeam-B_Silkscreen.gbr, AbuDhabi_ElectronBeam-Edge_Cuts.gbr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]
2025-02-13 changes in new pcb
    [Final_PCB.kicad_pcb, SC1.kicad_sch]
2025-02-16 a lot of advance in final PCB
    [Artikelliste.xlsx, Final_PCB.kicad_pcb, Final_PCB.kicad_sch, sensors.kicad_sch]
2025-02-18 still need to finish routing
    [Final_PCB.kicad_pcb, Final_PCB.kicad_sch, pre_filter.kicad_sch]
2025-02-18 Almost done with routing
    [Final_PCB.kicad_pcb, Final_PCB.kicad_sch]
2025-02-19 final PCB finished
    [Final_PCB.kicad_pcb, Final_PCB.kicad_sch, Signal_cond.kicad_sch, sensors.kicad_sch]
2025-02-19 Added grid voltage connector
    [Final_PCB.kicad_pcb, Final_PCB.kicad_sch]
2025-02-20 Commit before changing PCB connectors, just in case
    [Final_PCB.kicad_pcb, Final_PCB.kicad_sch, bomlist.csv]
2025-02-20 Changed connectors according to stock. Added auxiliar projects for printing each PCB, added component list
    [Artikelliste.xlsx, Final_PCB.kicad_pcb, Final_PCB.kicad_sch, LP_SC_PCB.kicad_pcb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]
2025-02-20 bom_list file from kicad added
    [bom_file.csv]
2025-02-24 adding some matlab simulations and graphs
    [Final_PCB.kicad_pcb, Platte.kicad_pcb]
2025-02-28 just committing local changes
    [Artikelliste.xlsx, Final_PCB.kicad_pcb]
2025-02-28 added 3D milling part
2025-03-10 updated Arduino code
2025-03-11 small changes on Arduino code
2025-03-11 added python code for visualizing currents
